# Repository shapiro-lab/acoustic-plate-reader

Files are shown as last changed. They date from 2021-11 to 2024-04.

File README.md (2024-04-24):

# Acoustic Plate Reader
# Introduction

This repository contains instructions for building and using an Acoustic Plate Reader (APR) to image bacterial or mammalian cell samples expressing gas vesicles (GVs) in high throughput using ultrasound.

The APR uses a Verasonics Vantage™ Research Ultrasound System for ultrasound image acquisition, and a custom-built motorized stage to raster scan the ultrasound transducer over the samples. The ultrasound image acquisition and transducer movement are controlled using custom MATLAB scripts run from the Vantage™ host computer. Data acquisition and analysis are automated via MATLAB GUIs.

Please consult the [preprint](https://doi.org/10.1101/2024.03.30.587094) for an example of how the APR was used to evolve bacterial acoustic reporter genes for increased nonlinear ultrasound contrast.

SupplementaryVideo1-ezgif com-video-to-gif-converter-2

# Construction
APR
## Motorized stage
The motorized stage setup used to scan the transducer over the samples consists of three components: the stage itself, the acrylic base that supports it, and the MATLAB scripts used to control it. The scripts can be found [here](https://github.com/drmittelstein/ultrasound_hardware_control?tab=readme-ov-file#scripts-in-this-repository), but are provided only for troubleshooting purposes; the control of the stage during a scan is built into the Data Acquisition GUI. The parts required to build the stage and base are provided in the tables below; the assembly of the stage is self-explanatory, and the CAD files for machining the base can be found [here](https://github.com/drmittelstein/ultrasound_rigs/tree/master/Mech%20Translating%20Stage%20Setup).

**Motorized stage: BiSlide Motorized Translating System: 24”, 12”, 8”, (5 um resolution) from Velmex**

Screenshot 2024-04-23 at 2 57 05 PM

| Velmex catalog number | Part name                                                   | Part role      |
|-----------------------|-------------------------------------------------------------|----------------|
| MN10-0240-M02-21      | BiSlide, T=24", 2mm/rev, limits, NEMA 23 mount             | X-axis BiSlide |
| PK266-03A-P1         | Vexta Type 23T2, Single Shaft Stepper Motor                | X-axis BiSlide |
| MC-3                  | Cleat, 2 hole BiSlide for English or Metric optical tables | X-axis BiSlide |
| MB-1                  | BiSlide Bolt 1/4-20x3/4" Socket cap screw (10 pack)        | X-axis BiSlide |
| MN10-0120-M02-21      | BiSlide, travel=12 inch, 2 mm/rev, limits, NEMA 23        | Y-axis BiSlide |
| PK266-03A-P1         | Vexta Type 23T2, Single Shaft Stepper Motor                | Y-axis BiSlide |
| MC-2                  | Cleat, 2 hole BiSlide                                      | Y-axis BiSlide |
| MN10-0080-M02-21      | BiSlide, travel=8 inch, 2 mm/rev, limits, NEMA 23         | Z-axis BiSlide |
| PK266-03B-P2         | Vexta Type 23T2, Double Shaft Stepper Motor               | Z-axis BiSlide |
| D6CL-6.3F             | D6CL Damper for Type 23 Double Shaft Stepper Motor         | Z-axis BiSlide |
| VXM-3              | Control, 3-axis programmable stepping motor control         | Motor controller |
| VXM-USB-RS232         | USB to RS232 Serial Communication Cable 10ft              | Cable |

**Acrylic base**

| McMaster-Carr catalog number | Material name                                                    | Material role        |
|------------------------------|------------------------------------------------------------------|----------------------|
| 8560K325                     | Clear Scratch- and UV-Resistant Cast Acrylic Sheet (24" x 36" x 1") | Base                 |
| 8560K914                     | Clear Scratch- and UV-Resistant Cast Acrylic Sheet (12" x 12" x 2") | Material to make pillars |
| 1227T459                    | Clear Scratch- and UV-Resistant Cast Acrylic Bar (3" Wide x 1/2" Thick) | Material to make adapters |

Dimensions of mounted stage: 18” x 28”

Screenshot 2024-04-23 at 2 59 03 PM

## Imaging water tank
The water tank used in this study is designed to hold 12 of the 96-well phantoms. The parts were made by laser cutting, assembled with SCIGRIP Weld-On #4, and water-proofed with a silicone sealant. For the walls (Long_v4.DXF and Short_v4.DXF) and the base insert (Base_horiz.DXF), 0.25" acrylic sheets were used, while for the bottom piece (Inner.DXF), 0.5" ones were used for improved rigidity. Alternatively, two pieces of the bottom cut from 0.25" acrylic sheets can be stacked and glued together. The simulated full assembly of the tank is shown in Full_Assemble.SLDASM for reference.
## 96-well phantoms
The phantom molds were 3D-printed (96-well_PhantomMold_v1.STL and 96-well_PhantomMold_body_shallow.STL). Specifically, the molding parts (96-well_PhantomMold_v1.STL) were printed with Nylon 12 using Selective Laser Sintering through Shapeways for the finer features of the wells. The walls (96-well_PhantomMold_body_shallow.STL) were printed with PLA in-house. 
## Transducer holders
The holder for the transducer used in this study (Verasonics L22-14vX) was 3D-printed with PLA in-house (L22_holder_15deg.SLDPRT and L22_holder_top.SLDPRT).

# Sample preparation
APR Workflow
1) Preparation of *E. coli* cells expressing GVs
2) Casting of a 96-well agarose phantom
3) Preparation of low-melt molten agarose for loading *E. coli* samples into the phantom
4) Loading of samples into the phantom at 42C
5) Scanning of the loaded phantom using the Acoustic Plate Reader

# Running a scan
## Types of scans
The most common types of scans we run are:
* Pre-/post-collapse imaging: this is the fastest scan type, and is good for checking if samples are producing GVs or not. It requires that you know the appropriate voltage to image your GV type of interest without collapsing them, which can be determined from an imaging voltage ramp.
* Imaging voltage ramps: this scan type is useful for characterizing the way a GV type responds to varying acoustic pressure, either to find a pressure that will image the GVs without collapsing them or for other applications like multiplexed imaging.
* Collapse voltage ramps: this scan type will acquire acoustic collapse data for your samples. Imaging is performed using whatever "beam type" is specified (xAM recommended), and collapse is performed using a parabolic beam.

## Starting a scan via the GUI
1. Enter the name you wish the data folder to have in the "save name" field
2. Click "Select Vantage directory" and navigate to the Vantage directory you wish to run the data acquisition script from (this will likely have a name of the form "Vantage-4.6.2-XXX" and should contain a script called "activate.p"
3. Select the transducer, beam type, plate parameters, and number of equilibration frames you want. You will rarely need to change the starting well/row/column fields, and you should make sure that the numbers of rows/columns matches the number of plates you wish to scan. If you set these numbers to be too high, the motor stage will not automatically recognize this error, and may damage the transducer. The number of equilibration frames is the number of frames that occur between a change in voltage and the imaging being saved for that voltage, and is intended to make sure that if any GVs are going to collapse at that imaging voltage, they do so before the final image for that voltage is aquired.
4. Select the scan type, and set the voltages for the scan as desired.
5. Confirm that everything is correct, and click "Start Scan"



6. Looking at the gray Bmode iamge, posisiton the first well as it appears in the screenshot. The depth will depend on the transducer used: the sample should be at 5 mm for the L22, and 20 mm for the L10.
7. In the gray VSX GUI, click "Start Ramp" (you may have to click it many times for the scan to start).

# Processing data
The Data Processing GUI was designed to process data for any of the three scan types that was acquired using the Data Acquisition GUI. 

## Processing data via the GUI

# Common issues
## Unable to connect to motor stage
Open Device Manager, and under Ports, look for "Prolific USB-to-Serial Comm Port (COM2)". If the device doesn't show up, restart and replug the motor stage. If it shows up in the list but isn't on COM2, go to Properties->Port Settings->Advanced and switch it. If this doesn't work, try re-installing the driver for the motor stage from the Velmex website.
## Scan stops before finishing
This is usually caused by a problem connecting with the motor stage, or rarely by a Windows Update that forces the computer to restart.

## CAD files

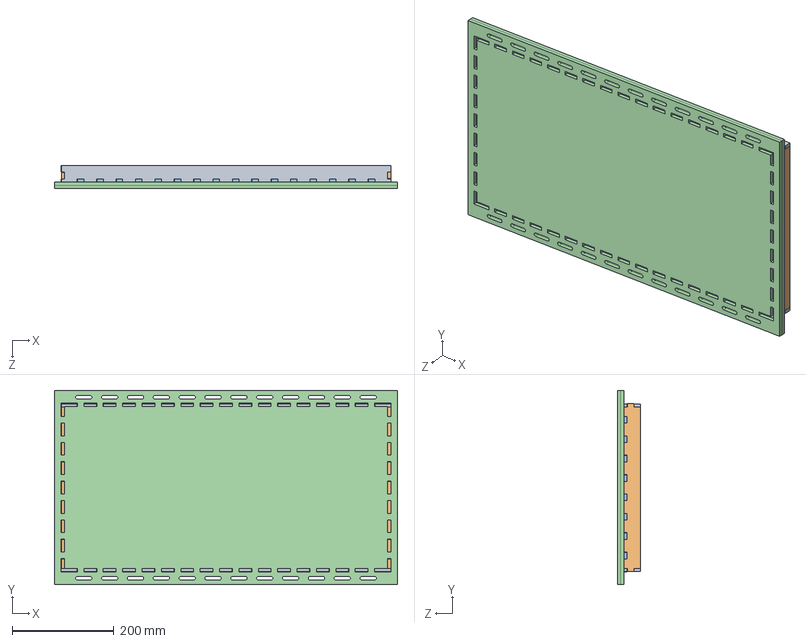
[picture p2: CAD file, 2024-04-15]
Construction/Full_Assemble.SLDASM
674.1 x 382.0 x 45.4 mm
Long_v2 x 2
Short_v4 x 2
Base_horiz_v2
Inner x 2

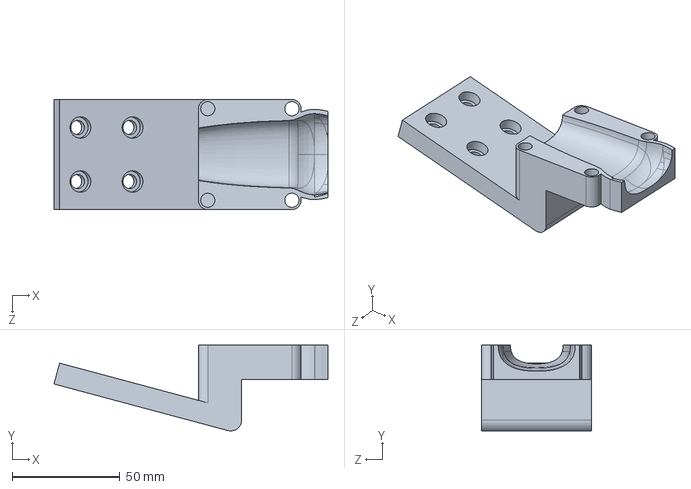
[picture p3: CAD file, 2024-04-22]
Construction/L22_holder_15deg.SLDPRT
126.9 x 39.8 x 51.0 mm

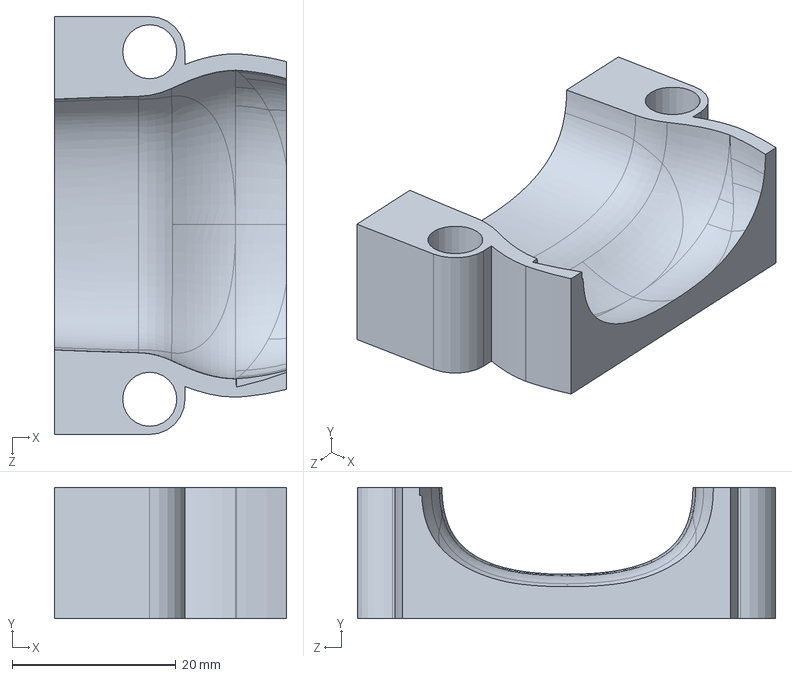
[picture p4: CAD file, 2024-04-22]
Construction/L22_holder_top.SLDPRT
28.4 x 16.0 x 51.0 mm

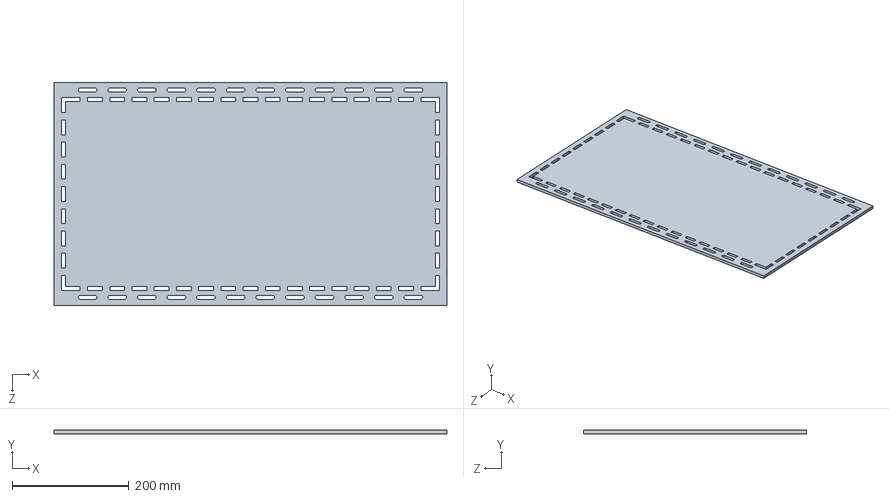
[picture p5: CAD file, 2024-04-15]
Construction/Inner.SLDPRT
674.1 x 6.35 x 382.0 mm

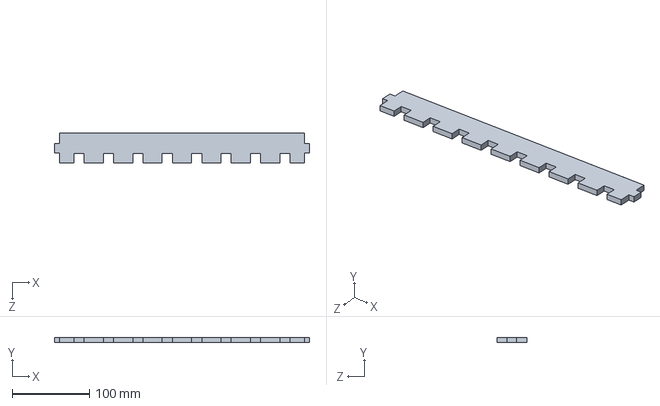
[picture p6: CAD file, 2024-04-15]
Construction/Short_v4.SLDPRT
330.2 x 6.35 x 38.4 mm

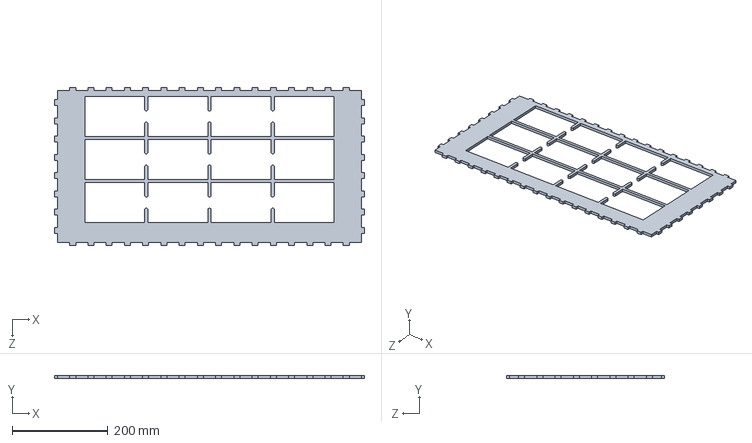
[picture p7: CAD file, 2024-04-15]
Construction/Base_horiz_v2.SLDPRT
647.7 x 6.35 x 330.2 mm

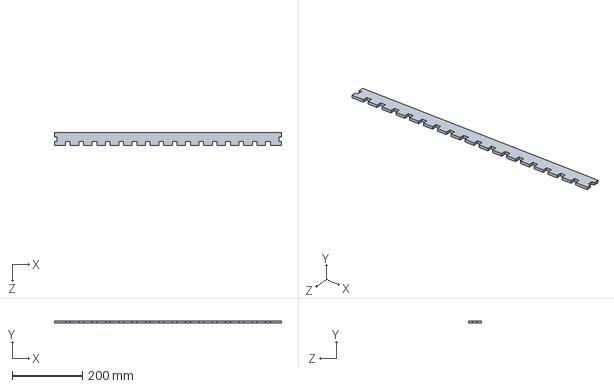
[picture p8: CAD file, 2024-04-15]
Construction/Long_v4.SLDPRT
647.7 x 6.35 x 37.8 mm

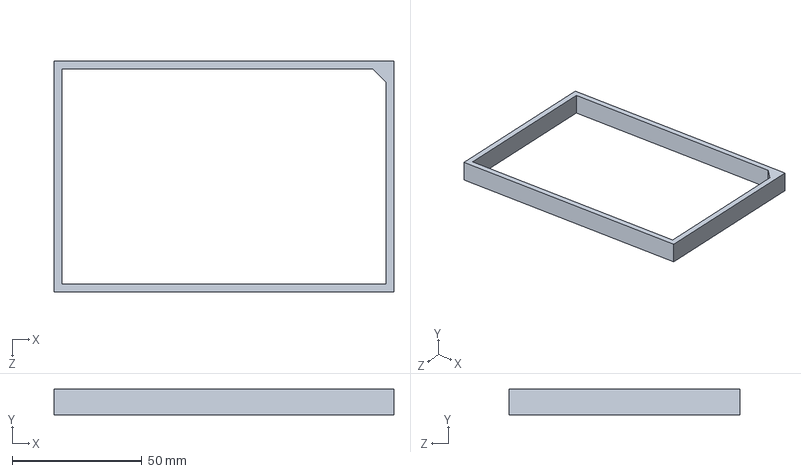
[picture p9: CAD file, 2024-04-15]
Construction/96-well_PhantomMold_body_shallow.SLDPRT
131.0 x 10.0 x 89.0 mm

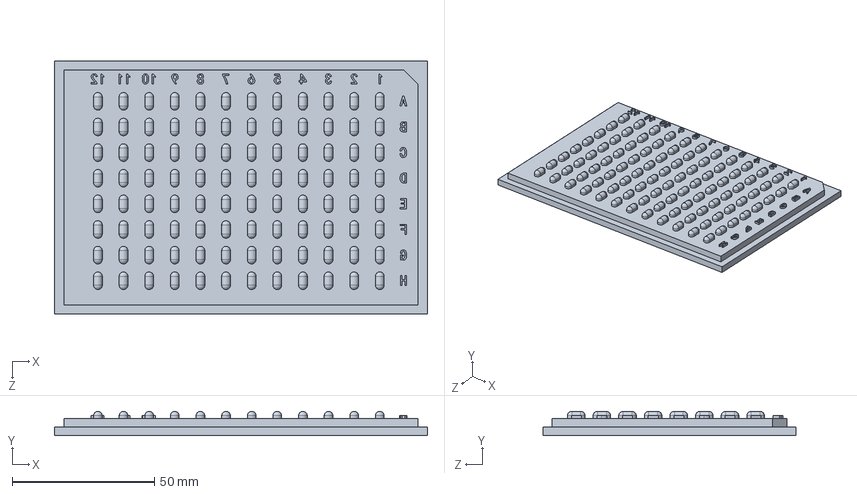
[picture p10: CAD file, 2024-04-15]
Construction/96-well_PhantomMold_v1.SLDPRT
131.0 x 8.55 x 89.0 mm

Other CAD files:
Construction/96-well_PhantomMold_body_shallow.STL
Construction/Base_horiz_v2.DXF
Construction/Inner.DXF
Construction/Long_v4.DXF
Construction/Short_v4.DXF

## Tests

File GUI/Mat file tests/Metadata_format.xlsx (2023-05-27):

Well | SampleName | Temp_C | inducer_name | Inducer_conc_uM | glucose_conc_%
A1 | pMetTU1-A_Sv5K_araC-PBAD_MCD1_AnaA_lib-acceptor-1_trunc-3UTR_T_AnaCNJKFGW | 30 | IPTG | 0 | 0
B1 | pMetTU1-A_Sv5K_araC-PBAD_MCD1_AnaA_lib-acceptor-1_trunc-3UTR_T_AnaCNJKFGW | 30 | IPTG | 0.1 | 0
C1 | pMetTU1-A_Sv5K_araC-PBAD_MCD1_AnaA_lib-acceptor-1_trunc-3UTR_T_AnaCNJKFGW | 30 | IPTG | 1 | 0
D1 | pMetTU1-A_Sv5K_araC-PBAD_MCD1_AnaA_lib-acceptor-1_trunc-3UTR_T_AnaCNJKFGW | 30 | IPTG | 5 | 0
E1 | pMetTU1-A_Sv5K_araC-PBAD_MCD1_AnaA_lib-acceptor-1_trunc-3UTR_T_AnaCNJKFGW | 30 | IPTG | 10 | 0
F1 | pMetTU1-A_Sv5K_araC-PBAD_MCD1_AnaA_lib-acceptor-1_trunc-3UTR_T_AnaCNJKFGW | 30 | IPTG | 50 | 0
G1 | pMetTU1-A_Sv5K_araC-PBAD_MCD1_AnaA_lib-acceptor-1_trunc-3UTR_T_AnaCNJKFGW | 30 | IPTG | 100 | 0
H1 | pMetTU1-A_Sv5K_araC-PBAD_MCD1_AnaA_lib-acceptor-1_trunc-3UTR_T_AnaCNJKFGW | 30 | IPTG | 500 | 0
A2 | pMetTU1-A_Sv5K_araC-PBAD_MCD1_AnaA_lib-acceptor-1_trunc-3UTR_T_AnaCNJKFGW | 30 | IPTG | 0 | 0.1
B2 | pMetTU1-A_Sv5K_araC-PBAD_MCD1_AnaA_lib-acceptor-1_trunc-3UTR_T_AnaCNJKFGW | 30 | IPTG | 0.1 | 0.1
C2 | pMetTU1-A_Sv5K_araC-PBAD_MCD1_AnaA_lib-acceptor-1_trunc-3UTR_T_AnaCNJKFGW | 30 | IPTG | 1 | 0.1
D2 | pMetTU1-A_Sv5K_araC-PBAD_MCD1_AnaA_lib-acceptor-1_trunc-3UTR_T_AnaCNJKFGW | 30 | IPTG | 5 | 0.1
E2 | pMetTU1-A_Sv5K_araC-PBAD_MCD1_AnaA_lib-acceptor-1_trunc-3UTR_T_AnaCNJKFGW | 30 | IPTG | 10 | 0.1
F2 | pMetTU1-A_Sv5K_araC-PBAD_MCD1_AnaA_lib-acceptor-1_trunc-3UTR_T_AnaCNJKFGW | 30 | IPTG | 50 | 0.1
G2 | pMetTU1-A_Sv5K_araC-PBAD_MCD1_AnaA_lib-acceptor-1_trunc-3UTR_T_AnaCNJKFGW | 30 | IPTG | 100 | 0.1
H2 | pMetTU1-A_Sv5K_araC-PBAD_MCD1_AnaA_lib-acceptor-1_trunc-3UTR_T_AnaCNJKFGW | 30 | IPTG | 500 | 0.1
A3 | pMetTU1-A_Sv5K_araC-PBAD_MCD1_AnaA_lib-acceptor-1_trunc-3UTR_T_AnaCNJKFGW | 30 | IPTG | 0 | 0.2
B3 | pMetTU1-A_Sv5K_araC-PBAD_MCD1_AnaA_lib-acceptor-1_trunc-3UTR_T_AnaCNJKFGW | 30 | IPTG | 0.1 | 0.2
C3 | pMetTU1-A_Sv5K_araC-PBAD_MCD1_AnaA_lib-acceptor-1_trunc-3UTR_T_AnaCNJKFGW | 30 | IPTG | 1 | 0.2
D3 | pMetTU1-A_Sv5K_araC-PBAD_MCD1_AnaA_lib-acceptor-1_trunc-3UTR_T_AnaCNJKFGW | 30 | IPTG | 5 | 0.2
E3 | pMetTU1-A_Sv5K_araC-PBAD_MCD1_AnaA_lib-acceptor-1_trunc-3UTR_T_AnaCNJKFGW | 30 | IPTG | 10 | 0.2
F3 | pMetTU1-A_Sv5K_araC-PBAD_MCD1_AnaA_lib-acceptor-1_trunc-3UTR_T_AnaCNJKFGW | 30 | IPTG | 50 | 0.2
G3 | pMetTU1-A_Sv5K_araC-PBAD_MCD1_AnaA_lib-acceptor-1_trunc-3UTR_T_AnaCNJKFGW | 30 | IPTG | 100 | 0.2
H3 | pMetTU1-A_Sv5K_araC-PBAD_MCD1_AnaA_lib-acceptor-1_trunc-3UTR_T_AnaCNJKFGW | 30 | IPTG | 500 | 0.2
A4 | pMetTU1-A_Sv5K_araC-PBAD_MCD1_AnaA_lib-acceptor-1_trunc-3UTR_T_AnaCNJKFGW | 30 | IPTG | 0 | 0.3
B4 | pMetTU1-A_Sv5K_araC-PBAD_MCD1_AnaA_lib-acceptor-1_trunc-3UTR_T_AnaCNJKFGW | 30 | IPTG | 0.1 | 0.3
C4 | pMetTU1-A_Sv5K_araC-PBAD_MCD1_AnaA_lib-acceptor-1_trunc-3UTR_T_AnaCNJKFGW | 30 | IPTG | 1 | 0.3
D4 | pMetTU1-A_Sv5K_araC-PBAD_MCD1_AnaA_lib-acceptor-1_trunc-3UTR_T_AnaCNJKFGW | 30 | IPTG | 5 | 0.3
E4 | pMetTU1-A_Sv5K_araC-PBAD_MCD1_AnaA_lib-acceptor-1_trunc-3UTR_T_AnaCNJKFGW | 30 | IPTG | 10 | 0.3
F4 | pMetTU1-A_Sv5K_araC-PBAD_MCD1_AnaA_lib-acceptor-1_trunc-3UTR_T_AnaCNJKFGW | 30 | IPTG | 50 | 0.3
G4 | pMetTU1-A_Sv5K_araC-PBAD_MCD1_AnaA_lib-acceptor-1_trunc-3UTR_T_AnaCNJKFGW | 30 | IPTG | 100 | 0.3
H4 | pMetTU1-A_Sv5K_araC-PBAD_MCD1_AnaA_lib-acceptor-1_trunc-3UTR_T_AnaCNJKFGW | 30 | IPTG | 500 | 0.3
A5 | pMetTU1-A_Sv5K_araC-PBAD_MCD1_AnaA_lib-acceptor-1_trunc-3UTR_T_AnaCNJKFGW | 30 | IPTG | 0 | 0.4
B5 | pMetTU1-A_Sv5K_araC-PBAD_MCD1_AnaA_lib-acceptor-1_trunc-3UTR_T_AnaCNJKFGW | 30 | IPTG | 0.1 | 0.4
C5 | pMetTU1-A_Sv5K_araC-PBAD_MCD1_AnaA_lib-acceptor-1_trunc-3UTR_T_AnaCNJKFGW | 30 | IPTG | 1 | 0.4
D5 | pMetTU1-A_Sv5K_araC-PBAD_MCD1_AnaA_lib-acceptor-1_trunc-3UTR_T_AnaCNJKFGW | 30 | IPTG | 5 | 0.4
E5 | pMetTU1-A_Sv5K_araC-PBAD_MCD1_AnaA_lib-acceptor-1_trunc-3UTR_T_AnaCNJKFGW | 30 | IPTG | 10 | 0.4
F5 | pMetTU1-A_Sv5K_araC-PBAD_MCD1_AnaA_lib-acceptor-1_trunc-3UTR_T_AnaCNJKFGW | 30 | IPTG | 50 | 0.4
G5 | pMetTU1-A_Sv5K_araC-PBAD_MCD1_AnaA_lib-acceptor-1_trunc-3UTR_T_AnaCNJKFGW | 30 | IPTG | 100 | 0.4
H5 | pMetTU1-A_Sv5K_araC-PBAD_MCD1_AnaA_lib-acceptor-1_trunc-3UTR_T_AnaCNJKFGW | 30 | IPTG | 500 | 0.4
A6 | pMetTU1-A_Sv5K_araC-PBAD_MCD1_AnaA_lib-acceptor-1_trunc-3UTR_T_AnaCNJKFGW | 30 | IPTG | 0 | 0.5
B6 | pMetTU1-A_Sv5K_araC-PBAD_MCD1_AnaA_lib-acceptor-1_trunc-3UTR_T_AnaCNJKFGW | 30 | IPTG | 0.1 | 0.5
C6 | pMetTU1-A_Sv5K_araC-PBAD_MCD1_AnaA_lib-acceptor-1_trunc-3UTR_T_AnaCNJKFGW | 30 | IPTG | 1 | 0.5
D6 | pMetTU1-A_Sv5K_araC-PBAD_MCD1_AnaA_lib-acceptor-1_trunc-3UTR_T_AnaCNJKFGW | 30 | IPTG | 5 | 0.5
E6 | pMetTU1-A_Sv5K_araC-PBAD_MCD1_AnaA_lib-acceptor-1_trunc-3UTR_T_AnaCNJKFGW | 30 | IPTG | 10 | 0.5
F6 | pMetTU1-A_Sv5K_araC-PBAD_MCD1_AnaA_lib-acceptor-1_trunc-3UTR_T_AnaCNJKFGW | 30 | IPTG | 50 | 0.5
G6 | pMetTU1-A_Sv5K_araC-PBAD_MCD1_AnaA_lib-acceptor-1_trunc-3UTR_T_AnaCNJKFGW | 30 | IPTG | 100 | 0.5
H6 | pMetTU1-A_Sv5K_araC-PBAD_MCD1_AnaA_lib-acceptor-1_trunc-3UTR_T_AnaCNJKFGW | 30 | IPTG | 500 | 0.5
A7 | pMetTU1-A_Sv5K_araC-PBAD_MCD1_AnaA_lib-acceptor-2_trunc-3UTR_T_AnaCNJKFGW | 37 | Arabinose | 0 | 0
B7 | pMetTU1-A_Sv5K_araC-PBAD_MCD1_AnaA_lib-acceptor-2_trunc-3UTR_T_AnaCNJKFGW | 37 | Arabinose | 0.0005 | 0
C7 | pMetTU1-A_Sv5K_araC-PBAD_MCD1_AnaA_lib-acceptor-2_trunc-3UTR_T_AnaCNJKFGW | 37 | Arabinose | 0.001 | 0
D7 | pMetTU1-A_Sv5K_araC-PBAD_MCD1_AnaA_lib-acceptor-2_trunc-3UTR_T_AnaCNJKFGW | 37 | Arabinose | 0.005 | 0
E7 | pMetTU1-A_Sv5K_araC-PBAD_MCD1_AnaA_lib-acceptor-2_trunc-3UTR_T_AnaCNJKFGW | 37 | Arabinose | 0.01 | 0
F7 | pMetTU1-A_Sv5K_araC-PBAD_MCD1_AnaA_lib-acceptor-2_trunc-3UTR_T_AnaCNJKFGW | 37 | Arabinose | 0.05 | 0
G7 | pMetTU1-A_Sv5K_araC-PBAD_MCD1_AnaA_lib-acceptor-2_trunc-3UTR_T_AnaCNJKFGW | 37 | Arabinose | 0.1 | 0
H7 | pMetTU1-A_Sv5K_araC-PBAD_MCD1_AnaA_lib-acceptor-2_trunc-3UTR_T_AnaCNJKFGW | 37 | Arabinose | 1 | 0
A8 | pMetTU1-A_Sv5K_araC-PBAD_MCD1_AnaA_lib-acceptor-2_trunc-3UTR_T_AnaCNJKFGW | 37 | Arabinose | 0 | 0.1
B8 | pMetTU1-A_Sv5K_araC-PBAD_MCD1_AnaA_lib-acceptor-2_trunc-3UTR_T_AnaCNJKFGW | 37 | Arabinose | 0.0005 | 0.1
C8 | pMetTU1-A_Sv5K_araC-PBAD_MCD1_AnaA_lib-acceptor-2_trunc-3UTR_T_AnaCNJKFGW | 37 | Arabinose | 0.001 | 0.1
D8 | pMetTU1-A_Sv5K_araC-PBAD_MCD1_AnaA_lib-acceptor-2_trunc-3UTR_T_AnaCNJKFGW | 37 | Arabinose | 0.005 | 0.1
E8 | pMetTU1-A_Sv5K_araC-PBAD_MCD1_AnaA_lib-acceptor-2_trunc-3UTR_T_AnaCNJKFGW | 37 | Arabinose | 0.01 | 0.1
F8 | pMetTU1-A_Sv5K_araC-PBAD_MCD1_AnaA_lib-acceptor-2_trunc-3UTR_T_AnaCNJKFGW | 37 | Arabinose | 0.05 | 0.1
G8 | pMetTU1-A_Sv5K_araC-PBAD_MCD1_AnaA_lib-acceptor-2_trunc-3UTR_T_AnaCNJKFGW | 37 | Arabinose | 0.1 | 0.1
H8 | pMetTU1-A_Sv5K_araC-PBAD_MCD1_AnaA_lib-acceptor-2_trunc-3UTR_T_AnaCNJKFGW | 37 | Arabinose | 1 | 0.1
A9 | pMetTU1-A_Sv5K_araC-PBAD_MCD1_AnaA_lib-acceptor-2_trunc-3UTR_T_AnaCNJKFGW | 37 | Arabinose | 0 | 0.2
B9 | pMetTU1-A_Sv5K_araC-PBAD_MCD1_AnaA_lib-acceptor-2_trunc-3UTR_T_AnaCNJKFGW | 37 | Arabinose | 0.0005 | 0.2
C9 | pMetTU1-A_Sv5K_araC-PBAD_MCD1_AnaA_lib-acceptor-2_trunc-3UTR_T_AnaCNJKFGW | 37 | Arabinose | 0.001 | 0.2
D9 | pMetTU1-A_Sv5K_araC-PBAD_MCD1_AnaA_lib-acceptor-2_trunc-3UTR_T_AnaCNJKFGW | 37 | Arabinose | 0.005 | 0.2
E9 | pMetTU1-A_Sv5K_araC-PBAD_MCD1_AnaA_lib-acceptor-2_trunc-3UTR_T_AnaCNJKFGW | 37 | Arabinose | 0.01 | 0.2
F9 | pMetTU1-A_Sv5K_araC-PBAD_MCD1_AnaA_lib-acceptor-2_trunc-3UTR_T_AnaCNJKFGW | 37 | Arabinose | 0.05 | 0.2
G9 | pMetTU1-A_Sv5K_araC-PBAD_MCD1_AnaA_lib-acceptor-2_trunc-3UTR_T_AnaCNJKFGW | 37 | Arabinose | 0.1 | 0.2
H9 | pMetTU1-A_Sv5K_araC-PBAD_MCD1_AnaA_lib-acceptor-2_trunc-3UTR_T_AnaCNJKFGW | 37 | Arabinose | 1 | 0.2
A10 | pMetTU1-A_Sv5K_araC-PBAD_MCD1_AnaA_lib-acceptor-2_trunc-3UTR_T_AnaCNJKFGW | 37 | Arabinose | 0 | 0.3
B10 | pMetTU1-A_Sv5K_araC-PBAD_MCD1_AnaA_lib-acceptor-2_trunc-3UTR_T_AnaCNJKFGW | 37 | Arabinose | 0.0005 | 0.3
C10 | pMetTU1-A_Sv5K_araC-PBAD_MCD1_AnaA_lib-acceptor-2_trunc-3UTR_T_AnaCNJKFGW | 37 | Arabinose | 0.001 | 0.3
D10 | pMetTU1-A_Sv5K_araC-PBAD_MCD1_AnaA_lib-acceptor-2_trunc-3UTR_T_AnaCNJKFGW | 37 | Arabinose | 0.005 | 0.3
E10 | pMetTU1-A_Sv5K_araC-PBAD_MCD1_AnaA_lib-acceptor-2_trunc-3UTR_T_AnaCNJKFGW | 37 | Arabinose | 0.01 | 0.3
F10 | pMetTU1-A_Sv5K_araC-PBAD_MCD1_AnaA_lib-acceptor-2_trunc-3UTR_T_AnaCNJKFGW | 37 | Arabinose | 0.05 | 0.3
G10 | pMetTU1-A_Sv5K_araC-PBAD_MCD1_AnaA_lib-acceptor-2_trunc-3UTR_T_AnaCNJKFGW | 37 | Arabinose | 0.1 | 0.3
H10 | pMetTU1-A_Sv5K_araC-PBAD_MCD1_AnaA_lib-acceptor-2_trunc-3UTR_T_AnaCNJKFGW | 37 | Arabinose | 1 | 0.3
A11 | pMetTU1-A_Sv5K_araC-PBAD_MCD1_AnaA_lib-acceptor-2_trunc-3UTR_T_AnaCNJKFGW | 37 | Arabinose | 0 | 0.4
B11 | pMetTU1-A_Sv5K_araC-PBAD_MCD1_AnaA_lib-acceptor-2_trunc-3UTR_T_AnaCNJKFGW | 37 | Arabinose | 0.0005 | 0.4
C11 | pMetTU1-A_Sv5K_araC-PBAD_MCD1_AnaA_lib-acceptor-2_trunc-3UTR_T_AnaCNJKFGW | 37 | Arabinose | 0.001 | 0.4
D11 | pMetTU1-A_Sv5K_araC-PBAD_MCD1_AnaA_lib-acceptor-2_trunc-3UTR_T_AnaCNJKFGW | 37 | Arabinose | 0.005 | 0.4
E11 | pMetTU1-A_Sv5K_araC-PBAD_MCD1_AnaA_lib-acceptor-2_trunc-3UTR_T_AnaCNJKFGW | 37 | Arabinose | 0.01 | 0.4
F11 | pMetTU1-A_Sv5K_araC-PBAD_MCD1_AnaA_lib-acceptor-2_trunc-3UTR_T_AnaCNJKFGW | 37 | Arabinose | 0.05 | 0.4
G11 | pMetTU1-A_Sv5K_araC-PBAD_MCD1_AnaA_lib-acceptor-2_trunc-3UTR_T_AnaCNJKFGW | 37 | Arabinose | 0.1 | 0.4
H11 | pMetTU1-A_Sv5K_araC-PBAD_MCD1_AnaA_lib-acceptor-2_trunc-3UTR_T_AnaCNJKFGW | 37 | Arabinose | 1 | 0.4
A12 | pMetTU1-A_Sv5K_araC-PBAD_MCD1_AnaA_lib-acceptor-2_trunc-3UTR_T_AnaCNJKFGW | 37 | Arabinose | 0 | 0.5
B12 | pMetTU1-A_Sv5K_araC-PBAD_MCD1_AnaA_lib-acceptor-2_trunc-3UTR_T_AnaCNJKFGW | 37 | Arabinose | 0.0005 | 0.5
C12 | pMetTU1-A_Sv5K_araC-PBAD_MCD1_AnaA_lib-acceptor-2_trunc-3UTR_T_AnaCNJKFGW | 37 | Arabinose | 0.001 | 0.5
D12 | pMetTU1-A_Sv5K_araC-PBAD_MCD1_AnaA_lib-acceptor-2_trunc-3UTR_T_AnaCNJKFGW | 37 | Arabinose | 0.005 | 0.5
E12 | pMetTU1-A_Sv5K_araC-PBAD_MCD1_AnaA_lib-acceptor-2_trunc-3UTR_T_AnaCNJKFGW | 37 | Arabinose | 0.01 | 0.5
F12 | pMetTU1-A_Sv5K_araC-PBAD_MCD1_AnaA_lib-acceptor-2_trunc-3UTR_T_AnaCNJKFGW | 37 | Arabinose | 0.05 | 0.5
G12 | pMetTU1-A_Sv5K_araC-PBAD_MCD1_AnaA_lib-acceptor-2_trunc-3UTR_T_AnaCNJKFGW | 37 | Arabinose | 0.1 | 0.5
H12 | pMetTU1-A_Sv5K_araC-PBAD_MCD1_AnaA_lib-acceptor-2_trunc-3UTR_T_AnaCNJKFGW | 37 | Arabinose | 1 | 0.5

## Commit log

2022-08-04 put matlab app in separate folder
    [microtiter_data0001.csv]
2022-08-31 fixed voltage ramp slider
2022-09-27 more checks for Data Acq GUI, moved sub stage initialization to GUI script and stored updated DAQ script as DAQ_GUI_compatible
2022-12-29 Update autoROI3_v1.m
    sample ROI matching implemented.
2024-04-15 Adding 3D printing/laser cutting models
    [96-well_PhantomMold_body_shallow.SLDPRT, 96-well_PhantomMold_body_shallow.STL, 96-well_PhantomMold_v1.SLDPRT, Base_horiz_v2.DXF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]
2024-04-22 Typo correction
    [Full_Assemble.SLDASM]
2024-04-22 Add L22 holders
    [L22_holder_15deg.SLDPRT, L22_holder_top.SLDPRT]
